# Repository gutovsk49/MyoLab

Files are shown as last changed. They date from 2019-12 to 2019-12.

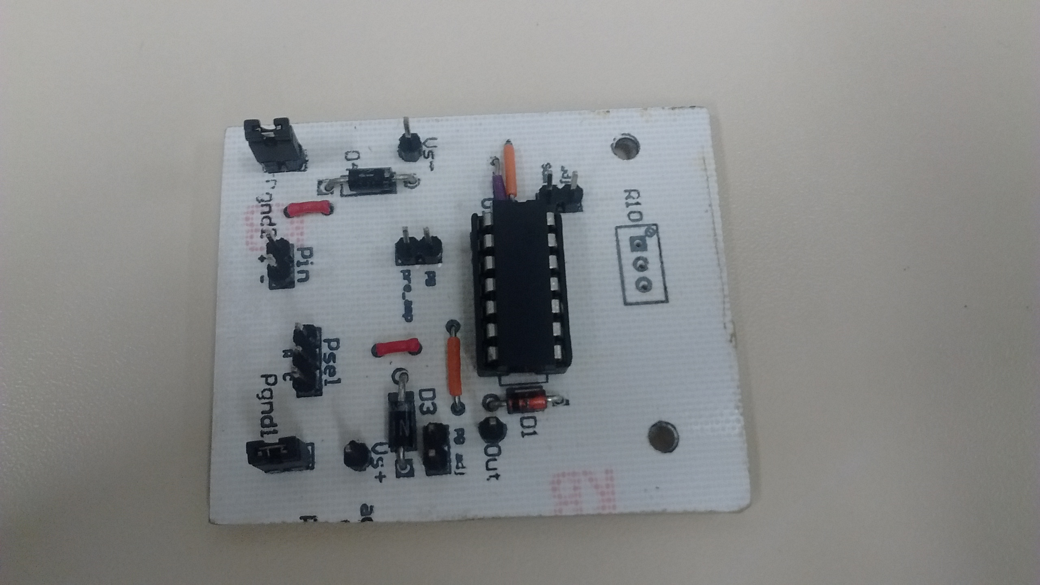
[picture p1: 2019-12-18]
prototipo_e_testes/IMG_20180618_203623081.jpg

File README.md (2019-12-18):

<h1> Sistema de aquisição de sinais elétricos musculares microcontrolado </h1>

<p>Repositorio criado para a disciplina de Projeto Integrador 3, do curso de engenharia eletrônica do IFSC - câmpus Florianópolis. <br/>
</p>

<h2> Revisão Bibliográfica </h2>

<p> A revisão bibliográfica pode ser acessada na wiki deste projeto.</p>
<p> A seguir, links de uma apresentação e um relatório técnico elaborados para outra disciplina, mas em cima do mesmo projeto, que podem ajudar na compreensão.<p>

[Apresentação - EMG](https://github.com/Everton-LF-Santos/Projeto-Integrador-3-2018-1/blob/Eletroneuromiografia-ENMG/prototipo_e_testes/Apresenta%C3%A7%C3%A3o%20PI3%20-%20COm.pdf)

[Relatório Técnico -EMG](https://docs.google.com/document/d/1B7dxLtk4YTgo0cG7-Vo4bE_Du3ThqNgDaQOGe45rIPg/edit)

<h2> Diagrama de blocos </h2>

Figura 1 - Diagrama de blocos do projeto Diagrama de Blocos

<h2> Pré-amplificador e filtro passa-alta </h2>
<p> Com a leitura das referências bilbiográficas da área feita e o diagrama de blocos definido, iniciou-se o desenvolvimento do projeto com o circuito de pré-amplificação. Foi encontrada no livro The Biomedical Engineering Book, uma topologia que junta o pré-amplificador e o filtro passa-alta no mesmo circuito. No exemplo da topologia, coincidentemente foi usado o INA118, mesmo amplificador de instrumentação disponível para o projeto. Na imagem a seguir, temos o esquemático simplificado e definição do ganho do componente.<p>
  
 Figura 2 - esquematico e ganho INA118 Esquemático simples e ganho INA118

<p>Foi arbitrado um ganho de 51 para a estrutura, por resultar em um valor de 1kohm para Rg, fácil de obter, e por ser um valor na faixa aceitável de ganho para esse tipo de estrutura neste tipo de aplicação, segundo a bibliografia estudada. A frequência de corte do passa-alta foi definida como 25 Hz, pois abaixo desse valor há ruídos de movimentação mecânica, e os diagramas de energia observados nas referências mostra a concentração de energia do sinal para a faixa acima deste valor.<p>
  
<p>Todas as considerações feitas, os cálculos e simulações pertinentes foram executados. Os arquivos de ambas etapas citadas estão disponível no link.<p>
  
Figura 3 - Circuito projetado Circuito projetado

[Calculos e Simulacoes - Pre_amp e PA](https://github.com/Everton-LF-Santos/Projeto-Integrador-3-2018-1/tree/Eletroneuromiografia-ENMG/pre_amp_e_passa_alta)

<h2> Filtro passa-baixa </h2>

<p>Com o primeiro bloco projetado, passou-se para o próximo bloco, o filtro passa-baixa. A topologia escolhida foi o filtro ativo Multiple Feedback com aproximação Butterworth. O ganho foi escolhido para 12,5 com o intuito de deixar o ganho em cascata da estrutura na casa das unidades de centenas. A frequência de corte de 250 Hz foi escolhida baseada no estudo dos diagramas de frequência do sinal  EMG. O ampop escolhido para implementar o circuito deste bloco foi o LM324, por atender as especificações de ganho e frequência e ser um componente de fácil obtenção e barato. Com os parâmetros do bloco definidos, passou-se então para os cálculos de componentes e simulações. Os arquivos pertinentes podem ser encontrados no link a seguir.<p>
  
Figura 4 - Circuito projetado Circuito projetado
  
[Calculos e Simulacoes - Filtro Passa-Baixa](https://github.com/Everton-LF-Santos/Projeto-Integrador-3-2018-1/tree/Eletroneuromiografia-ENMG/passa_baixa)

<h2> Somador DC </h2>

<p> A faixa de variação da amplitude do sinal elétrico muscular pode ser consideralmente ampla, devido fatores como tipo e qualidade dos eletrodos, grupo muscular em análise, capacidade e fisiologia do individuo em análise, entre outros. Levando isso em consideração, foi desenvolvido um bloco de ajuste de ganho, para que seja possível adequar o sinal adquirido da melhor forma possível.
<p>Porém, para fazer uma adequação correta, deve se conhecerou onde se está, e onde se quer chegar. O que temos são sinais da ordem de centenas de microvolts a unidades de milivolts. O que queremos é um sinal de saída analógico que pode ser convertido para informação digital, de preferência em um microncontrolador de baixo consumo. Estes geralmente trabalham com alimentação em 3.3 V. Logo, podemos definir que queremos um sinal de saída do módulo de aquisição que seja de 0 V a 3.3V, correspondente a sinais mioelétricos captados pelo eletrodo da ordem de 250uV até 5mV.
<p> Tendo o ponto de partida e de chegada, podemos focar esforços na construção do caminho. Para termos um sinal totalmente positivo na saída, é necessário que seja feito um offset DC no sinal. Para isso, foi escolhida a topologia de amplificador operacional na configuração não-inversora. Os valores de resistência do circuito foram arbitrados para não ter influencia no casamento de impedância dos blocos. A tensão de referência deste circuito (que deve ser metade da excursão do sinal de saída, logo, 3.3/2 = 1,65 V) será provida por um seguidor de tensão. Como o seguidor inverte a polaridade da tensão, o valor de -1,65V necessário é pego de um divisor resistivo entre o GND e o -5V da alimentação simétrica dos ampops.
<p> Tendo definido os parâmetros necessários, passaram-se para os demais cálculos e simulações do bloco de offset DC. Os arquivos relacionados a esta etapa podem ser encontrados no link.
  
Figura 5 - Circuito projetado Circuito projetado
  
[Calculos e Simulacoes - Somador DC](https://github.com/Everton-LF-Santos/Projeto-Integrador-3-2018-1/tree/Eletroneuromiografia-ENMG/somadorDC)

<h2> Ajuste de Ganho </h2>

<p> Devido a configuração e valores utilizados no bloco de offset DC, o sinal de entrada deste bloco deve variar de -0,815 V a +0,815 V para que haja 0 a 3.3V na saída. Com este faixa de amplitude necessária na entrada do bloco de offset, juntamente com a faixa de amplitude do sinal mioelétrico que deseja ser captada e conhecendo o ganho dos blocos anteriores, é possível finalmente projetar o bloco de ajuste de ganho. A topologia utilizada é simples, um amplificador operacional em configuração de ganho ajustável, com um trimpot conectado ao terminal inversor e na malha de realimentação e um diodo zener de 3.3V na saída para certificar que o valor máximo não seja ultrapassado. De acordo com os cálculos feitos, que podem ser observados nos arquivos desta etapa no link abaixo, o bloco de ajuste deve variar o ganho de aproximadamente 0,25 a 5. Conhecendo as impedâncias de entrada e saída dos blocos anteriores e posteriores, foram calculados os componentes necessários para que não houvesse influência na resposta em frequência do circuito. 
  
Figura 6 - Circuito projetado Circuito projetado
  
[Calculos e Simulacoes - Ajuste de ganho](https://github.com/Everton-LF-Santos/Projeto-Integrador-3-2018-1/tree/Eletroneuromiografia-ENMG/ajuste_ganho)
  
<h2> Prótotipo de aquisição e testes </h2>

<p> Com os quatro bloco de hardware de aquisição prontos, foi feito um protótipo para validar o funcionamento dos circuitos escolhidos. O esquemático e layout elaborados no software Altium Designer foram feitos em blocos, para garantir a validação individual de cada um, antes do teste coletivo. É possível acoplar os blocos por meio de jumpers. Após confeccionada a placa, foram feitos os testes pertinentes. Os resultados estão na apresentação de slides do link a seguir. Os outros arquivos relacionados à etapa de prototipagem e testes também podem ser encontrados no link.
  
Figura 7 - Blocos de hardware Blocos de hardware

Figura 8 - layout layout

Figura 9 - silk screen silk screen

Figura 10 - soldas SMD soldas SMD
  
[Protótipo  e teste do hardware de aquisição](https://github.com/Everton-LF-Santos/Projeto-Integrador-3-2018-1/tree/Eletroneuromiografia-ENMG/prototipo_e_testes)

<h2> Isolamento da rede e regulação de tensão </h2>

Com os resultados dos testes, foi concluído que os blocos do hardware de aquisição estavam de acordo com os requisitos necessários, porém para próxima etapa (teste IN VIVO), seria necessário que o circuito fosse alimentado de forma independente da rede elétrica. Assim, foi desenvolvida uma placa de regulação de tensão para alimentar o prototipo a partir de baterias 9 V. Os arquivos do projeto estão disponiveis no link a seguir.

[Placa de regulação de tensão](https://github.com/Everton-LF-Santos/Projeto-Integrador-3-2018-1/tree/Eletroneuromiografia-ENMG/reg_tensao)

<h2> Teste In Vivo </h2>

Com a alimentação regulada das baterias e sem interferência conduzida da rede elétrica, foi feito o teste In Vivo do hardware de aquisição. Usando eletrodos de Prata/Cloreto de Prata com gel condutor e cabos blindados, foi feita leitura do sinal da musculatura do antebraço esquerdo. O sinal foi observado por meio do osciloscópio portátil Rohde & Schwarz modelo RTH1004. Os arquivos relacionados a etapa de teste in vivo pode ser acessados pelo link a seguir.

[Teste In Vivo](https://github.com/Everton-LF-Santos/Projeto-Integrador-3-2018-1/tree/Eletroneuromiografia-ENMG/teste_vivo)

<h2> Teste In Vivo com transmissão dos dados </h2>

Por fim, foi iniciada a etapa de conversão analógica-digital transmissão dos dados, por meio do uso de um microcontrolador. Foi escolhido o chip ATMEGA328P pela experiência com desenvolvimentos anteriores. O código desenvolvido faz a conversão do sinal analógico em digital e envia o dado por meio do módulo Bluetooth HC-06. Para fins de facilitação de código, foi usada resolução de 8 bits na conversão A/D, com taxa de amostragem de 1 kHz. O uso de transmissão de dados sem fio é para garantir o isolamento galvânico do circuito de aquisição de qualquer outro equipamento eletrônico. Para visualização dos dados foi usado o software SerialPlot. Os arquivos relacionados a etapa de desenvolvimento do firmware, aquisição e visualização dos dados podem ser acessados no link a seguir.

[Teste In Vivo com aquisição de dados via Bluetooth](https://github.com/Everton-LF-Santos/Projeto-Integrador-3-2018-1/tree/Eletroneuromiografia-ENMG/firmware_bt)

<h2> Referências Bibliográficas </h2>

[link para arquivos das referências bibliográficas](https://drive.google.com/drive/u/1/folders/12AXk9AZwwBUo14S7_4OgoAu70kQn8SUb?ogsrc=32)

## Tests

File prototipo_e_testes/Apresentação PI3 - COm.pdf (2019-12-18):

# PROJETO INTEGRADOR III -MÓDULO DE AQUISIÇÃO DE SINAIS ELÉTRICOS MUSCULARES

Projeto IntegradorIII
Comunicação e Expressão
Augusto Daniel Rodrigues

## SUMÁRIO

- Sinais mioelétricos
- Condições de detecção de sinal
- Condicionamento de sinal
- Projeto dos blocos
- Esquemático, Layout e Hardware
- Testes dos blocos
- Referências

## SINAIS MIOELÉTRICOS

- Sinal sináptico -> axônio neuromotor -> potencial de ação;
- unidade motora;
- MUAP e MUAPT;
- Sinal EMG;

## SINAIS MIOELÉTRICOS

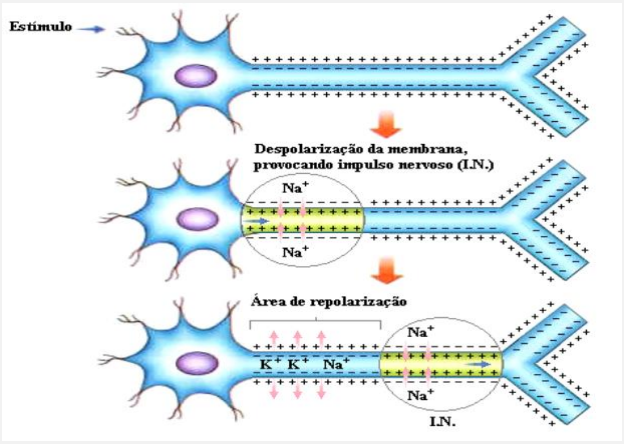
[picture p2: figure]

- Fonte:Vilela, 2004 apud Caparelli, 2007.

## SINAIS MIOELÉTRICOS

- Fonte:Vilela, 2004 apud Caparelli, 2007.

## SINAIS MIOELÉTRICOS

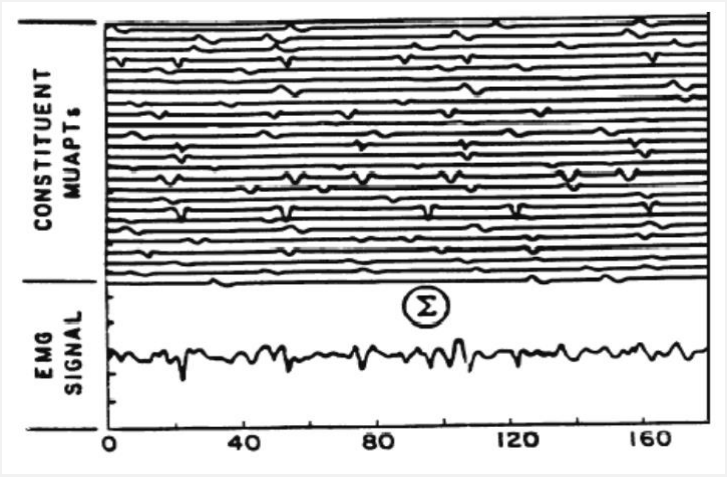
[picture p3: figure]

- Fonte: Basmajian; De Luca, 1985 apud Caparelli, 2007.

## CONDIÇÕES DE DETECÇÃO DO SINAL

- Eletrodos de agulha x eletrodos de superfície;
- Eletrodos passivos e ativos;
- 10mVpp e 10kHz x 5mVpp 250 Hz;
- Ruídos e interferências;
- Posicionamento dos eletrodos;
- Eletrodos de referência;
- Arranjos monopolar, bipolar, etc;

## CONDIÇÕES DE DETECÇÃO DO SINAL

- Ruídos e interferências;
- Cross Talk;
- Movimentos;
- EMI (rede elétrica);
- Componentes e técnicas de layout;

## SINAIS MIOELÉTRICOS

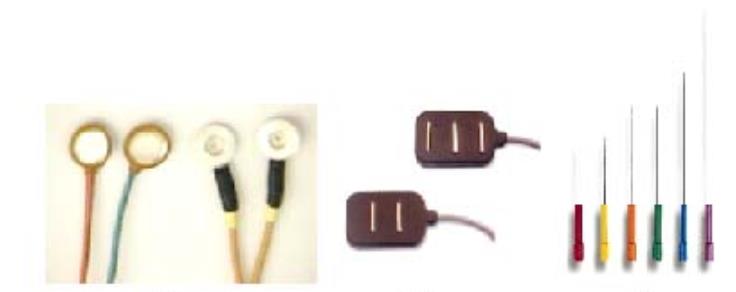
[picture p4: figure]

Fonte: Caparelli, 2007.

## SINAIS MIOELÉTRICOS

Fonte : https://www.primecirurgica.com.br/eletrodo-universal-red-dot-pct-c-50-unds-2570-3m-p760/

## SINAIS MIOELÉTRICOS

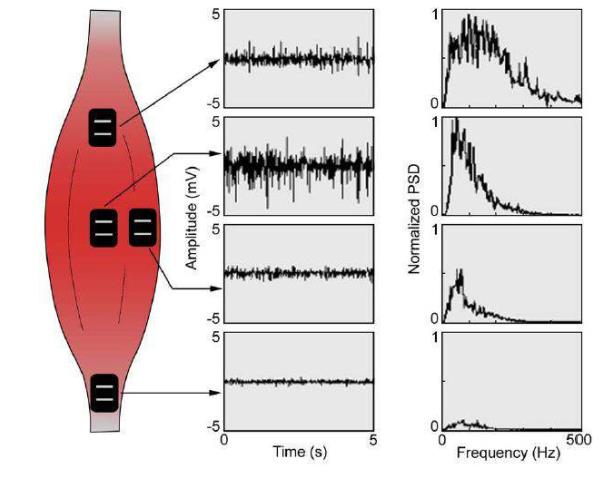
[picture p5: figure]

Fonte: Caparelli, 2007.

## CONDICIONAMENTO DO SINAL

- Amplificação do sinal;
- Filtragem em frequência;
- Offset DC;
- Conversão Analógica-Digital;
- Processamento;
- Visualização;

## CONDICIONAMENTO DO SINAL

- Amplificação do sinal;
- Amplificador de Instrumentação
- Amplificação diferencial;
- Alto CMRR;
- Ganho linear de até milhares de vezes;
- Alta impedância de entrada;

## CONDICIONAMENTO DO SINAL

Fonte: FRANCO, 1998 apud PEPINO, 2007.

## CONDICIONAMENTO DO SINAL

- Filtragem do sinal
- Anulação ou permissão do prosseguimento de um sinal em função de sua frequência;

## CONDICIONAMENTO DO SINAL

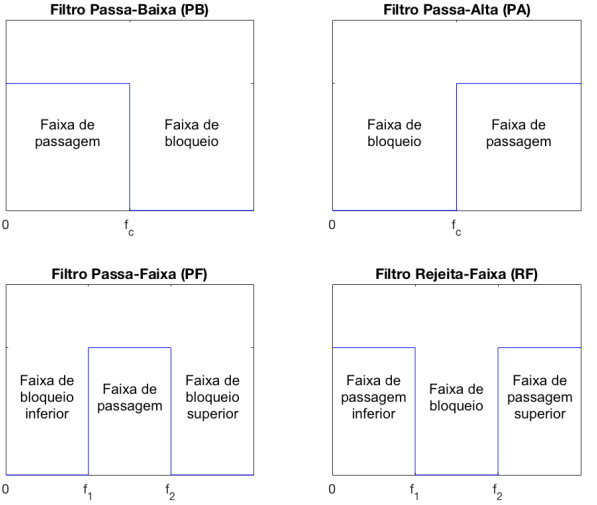
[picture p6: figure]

Fonte: LIMOLI (2017, p. 37).

## CONDICIONAMENTO DO SINAL

- Offset DC
- Elevação do nível de tensão do sinal;
- Sinal contínuo;
- Intervalo totalmente positivo (>=0);

## CONDICIONAMENTO DO SINAL

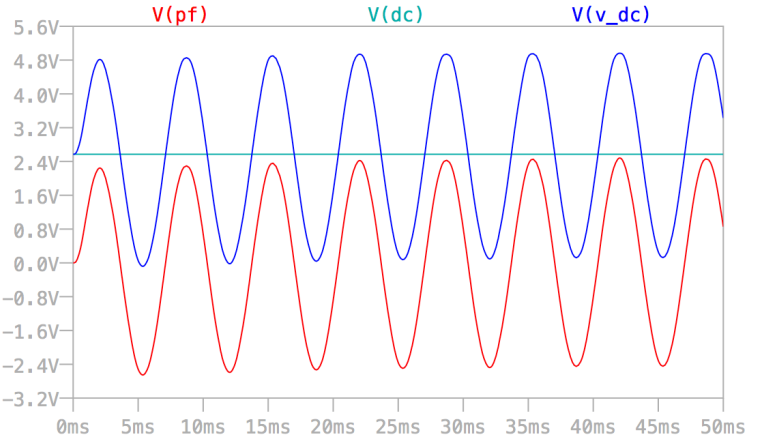
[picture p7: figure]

Fonte: LIMOLI (2017, p. 57).

## CONDICIONAMENTO DO SINAL

- Conversão Analógica-Digital
- Conversão de um nível de tensão para um conjunto de bits;
- Janela de conversão (1.1 V, 3.3 V, 5 V);
- Resolução da Conversão (nº de bits);
- Taxa de amostragem;

## CONDICIONAMENTO DO SINAL

Fonte: https://www.globalspec.com/learnmore/data_acquisition_signal_conditioning/signal_converting/analog_to_digital_converters

## PROJETO DOS BLOCOS

- Pré-requisitos / Parâmetros de projeto
- Conversão AD de 3.3 V 10 bits;
- Offset DC de 1,65 V;
- Janela de frequência de 25 Hz a 250 Hz;
- Considerar sinais da ordem de |250uV| à |5mV|;
- Ampop de instrumentação disponível = INA118;
- Ampop para demais circuitos = LM324N;
- Alimentação simétrica |5V| ( regulada de baterias de 9 V);

## PRÉ-AMPLIFICADOR + PASSA-ALTA

G = 51,
logo Rg = 1kΩ;

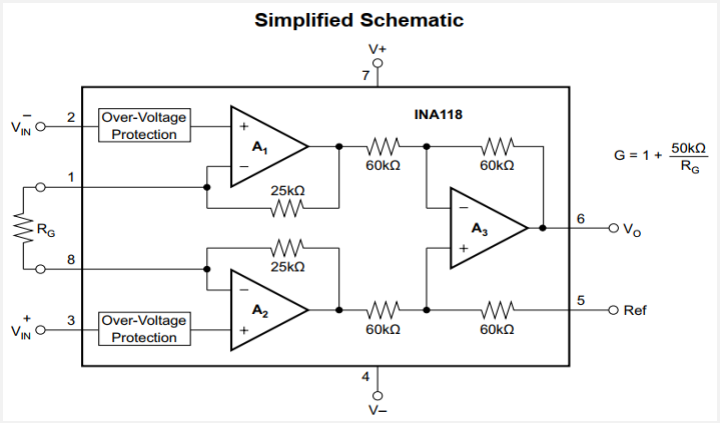
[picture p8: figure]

Fonte : Datasheet INA118. Disponível em : http://www.ti.com/lit/ds/symlink/ina118.pdf.

## PRÉ-AMPLIFICADOR + PASSA-ALTA

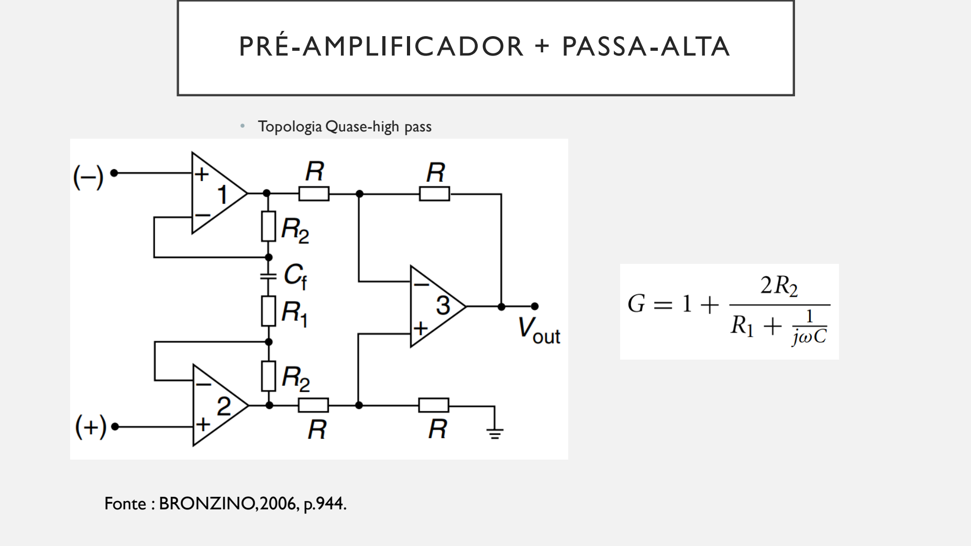
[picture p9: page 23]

- Topologia Quase-high pass

Fonte : BRONZINO, 2006, p.944.

## PRÉ-AMPLIFICADOR + PASSA-ALTA

Fonte: Do autor.

## PRÉ-AMPLIFICADOR + PASSA-ALTA

- Ganho = 51;
- Frequência de corte inferior = 25 Hz;
- C = 7 uF;

PRÉ -AMPLIFICADOR
+ PASSA-ALTA

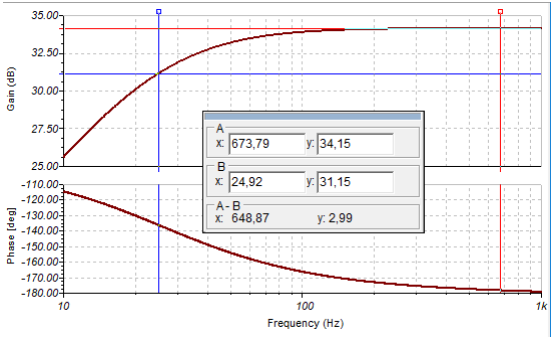
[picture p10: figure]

- Simulação
- 34,15 = 20*log(51)
- 31,15 = 20*log(51/√2)
- -3 dB;

Fonte: Do autor.

## PASSA-BAIXA

- Ganho = 12,5;
- Filtro ativo de 2ª ordem Multiple Feedback com aproximação Butterworth;
- Frequência de corte superior = 250 Hz;

## PASSA-BAIXA

Fonte: PERTENCE JR, Antônio (2003, p.184).

## PASSA-BAIXA

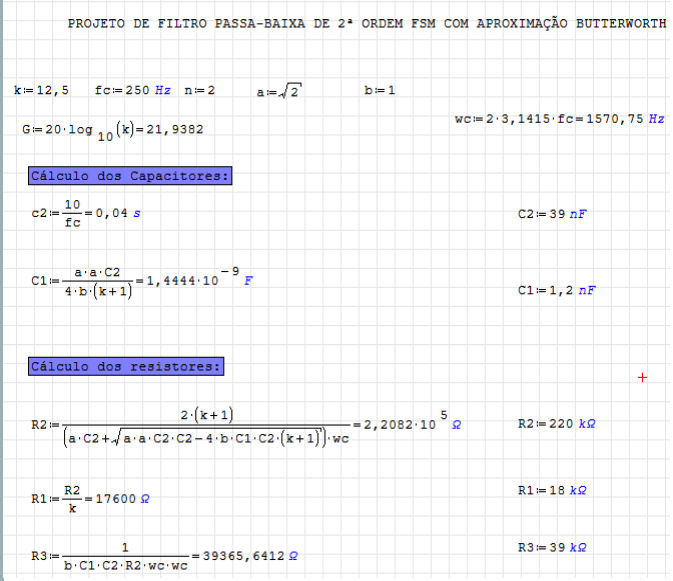
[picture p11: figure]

Fonte: Do autor.


## PASSA-BAIXA

- Simulação:
- Gs=10^(23,32/20) = 14,65
- Nova fc = 220 Hz (OK!)
- Ampop LM324N;

Fonte: Do autor.

## SOMADOR DC

- Saída de 0V a 3.3V;
- Buffer + somador não inversor;
- Capacitor de estabilização;
- Vref = 1,65V;
- Vout = 2*Vin +Vref, logo
- –0,815V <Vin < +0,815V
- Ampop LM324N;

Fonte: Do autor.

## SOMADOR DC

- Vref = -Vcc * R2 / (R1 + R2);
- R1 = 2,03*R2;
- R1 = 680k e R2 = 330k, Vref = 1,63 V;


Fonte: Do autor.

## AJUSTE DE GANHO

- Ganho do primeiro bloco = 51;
- Ganho do primeiro bloco = 12,5;
- Ganho em cascata = 637,5;
- Ganho máximo:
- |250uV| * 637,5 = 0,159375;
- 0,815 / 0,159375 = 5,11;
- Ganho mínimo:
- |5mV| * 637,5 = 3,1875;
- 0,815 / 3,1875 = 0,256;

## AJUSTE DE GANHO


- Capacitor de acoplamento AC;
- Situação 1:
- 56k/220k = 0,254;
- Situação 2:
- 1056k/220k = 4,8;

Fonte: Do autor.

## ESQUEMÁTICO, LAYOUT E HARDWARE

Fonte: Do autor.

## ESQUEMÁTICO, LAYOUT E HARDWARE


Fonte: Do autor.

## ESQUEMÁTICO, LAYOUT E HARDWARE


## ESQUEMÁTICO, LAYOUT E HARDWARE

Fonte: Do autor.

## ESQUEMÁTICO, LAYOUT E HARDWARE


Fonte: Do autor.

## ESQUEMÁTICO, LAYOUT E HARDWARE

Fonte: Do autor. | Fonte: Do autor. | Fonte: Do autor.

## ESQUEMÁTICO, LAYOUT E HARDWARE


Fonte: Do autor. | Fonte: Do autor.

## TESTES DOS BLOCOS


- Pré-amplificador + passa-alta:
- 3,68 / 77,6e-3 = 47,42;
- 500 Hz;
Fonte: Do autor. | Fonte: Do autor.

## TESTES DOS BLOCOS


- Pré-amplificador + passa-alta:
- 2,48 / 77,6e-3 = 31,96 ~= 47,42*0,707;
- ~27 Hz;
Fonte: Do autor. | Fonte: Do autor.

## TESTES DOS BLOCOS


- Passa-Baixa:
- 3,56/ 0,320 = 11,125;
- ~100 Hz;
Fonte: Do autor. | Fonte: Do autor.

## TESTES DOS BLOCOS

- Passa-Baixa:
- 3,72/ 0,316 = 11,77;
- ~27 Hz;


Fonte: Do autor.

## TESTES DOS BLOCOS

- Passa-Baixa:
- 2,60/ 0,318 = 8,17 ~= 11,77*0,707;
- ~250 Hz;

Fonte: Do autor.

## TESTES DOS BLOCOS

- Ajuste de Ganho:
- 2,90/ 0,624 = 4,64;


- ~150 Hz; | Fonte: Do autor.

## TESTES DOS BLOCOS

- Ajuste de Ganho:
- 0,556 / 2,06 = 0,269;


- ~150 Hz; | Fonte: Do autor.

## TESTES DOS BLOCOS


- Somador DC:
Fonte: Do autor. | Fonte: Do autor.

## OBRIGADO!

Augusto Daniel Rodrigues

augusto.dr@aluno.ifsc.edu.br

## REFERÊNCIAS

BRONZINO, Joseph D. The Biomedical Engineering Handbook: Medical Devices and Systems. 3th ed. Hartford. Taylor and Francis, 2006.
Disponível em:https://brainmaster.com/software/pubs/brain/The_Biomedical_Engineering_Handbook_.pdf

CAPARELLI, Thiago B. Projeto e desenvolvimento de um sistema multicanal de biotelemetria para detecção de sinais ECG, EEG e EMG. 2007. 109 p. Dissertação (Pós-graduação em Engenharia Elétrica) - Faculdade de Engenharia Elétrica, Universidade Federal de Uberlândia, Uberlândia.
Disponível em:https://repositorio.ufu.br/handle/123456789/14636

DE LUCA, Carlo J; BASMAJIAN, John V. Muscles Alive: Their functions revealed by eletromyography. 5th ed. Baltimore: Willians andWilkins, 1985.

LIMOLI, Camila S. Protótipo de um eletromiógrafo sem fio de baixo custo. 2017. 75 p. Trabalho de Conclusão de Curso (Graduação no Curso de Engenharia Elétrica com Ênfase em Eletrônica) - Escola de Engenharia de São Carlos, Universidade de São Paulo. - São Carlos.
Disponível em : http://www.tcc.sc.usp.br/tce/disponiveis/18/180450/tce-29052017-162649/?&lang=br

## REFERÊNCIAS

PEPINO, André L.G. Sistema de controle de Dispositivos Através de EMG(Eletromiografia). 2007. 90p. Monografia de Conclusão de Curso (Graduação em Engenharia da Computação) - Núcleo de Ciências Exatas e Tecnológicas, Centro Universitário Positivo. Curitiba.
Disponível em:https://www.up.edu.br/blogs/engenharia-da-computacao/wp-content/.../2007.1.pdf

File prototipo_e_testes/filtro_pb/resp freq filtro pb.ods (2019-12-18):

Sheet: teste 1 - filtro pb
f | Vin | Vout | G
1.000000 | 0,152 | 0,58 | 3,82
1.300000 | 0,152 | 0,62 | 4,08
1.690000 | 0,148 | 0,68 | 4,59
2.197000 | 0,148 | 0,66 | 4,46
2.856100 | 0,154 | 0,68 | 4,42
3.712930 | 0,152 | 0,7 | 4,61
4.826809 | 0,158 | 0,72 | 4,56
6.274852 | 0,156 | 0,68 | 4,36
8.157308 | 0,154 | 0,68 | 4,42
10.604500 | 0,166 | 0,68 | 4,10
13.785850 | 0,168 | 0,7 | 4,17
17.921604 | 0,168 | 0,68 | 4,05
23.298086 | 0,148 | 0,7 | 4,73
30.287512 | 0,148 | 0,7 | 4,73
39.373764 | 0,15 | 0,68 | 4,53
51.185894 | 0,16 | 0,7 | 4,38
66.541664 | 0,17 | 0,7 | 4,12
86.504166 | 0,156 | 0,68 | 4,36
112.455414 | 0,15 | 0,66 | 4,40
146.192032 | 0,168 | 0,64 | 3,81
190.049637 | 0,164 | 0,6 | 3,66
247.064529 | 0,158 | 0,5 | 3,16
321.183899 | 0,158 | 0,44 | 2,78
417.539063 | 0,158 | 0,3 | 1,90
542.800781 | 0,182 | 0,24 | 1,32
705.640991 | 0,16 | 0,16 | 1,00
917.333313 | 0,172 | 0,14 | 0,81
1192.533325 | 0,16 | 0,1 | 0,63
1550.293335 | 0,154 | 0,1 | 0,65
2015.381348 | 0,168 | 0,1 | 0,60
2619.995850 | 0,148 | 0,1 | 0,68
3405.994629 | 0,16 | 0,1 | 0,63
4427.792969 | 0,168 | 0,07 | 0,42
5756.130859 | 0,156 | 0,1 | 0,64
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

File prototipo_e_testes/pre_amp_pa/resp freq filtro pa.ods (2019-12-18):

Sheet: teste 1 - filtro pa + preamp
f | Vin | Vout | G
1.000000 | 0,202 | 0,32 | 1,58415841584158
1.300000 | 0,198 | 0,32 | 1,61616161616162
1.690000 | 0,19 | 0,48 | 2,52631578947368
2.197000 | 0,22 | 0,48 | 2,18181818181818
2.856100 | 0,182 | 0,48 | 2,63736263736264
3.712930 | 0,178 | 0,72 | 4,04494382022472
4.826809 | 0,184 | 0,64 | 3,47826086956522
6.274852 | 0,186 | 0,8 | 4,30107526881721
8.157308 | 0,202 | 0,96 | 4,75247524752475
10.604500 | 0,206 | 1,12 | 5,4368932038835
13.785850 | 0,228 | 1,44 | 6,31578947368421
17.921604 | 0,22 | 1,6 | 7,27272727272727
23.298086 | 0,204 | 1,92 | 9,41176470588235
30.287512 | 0,216 | 2,08 | 9,62962962962963
39.373764 | 0,204 | 2,24 | 10,9803921568627
51.185894 | 0,214 | 2,48 | 11,588785046729
66.541664 | 0,212 | 2,56 | 12,0754716981132
86.504166 | 0,202 | 2,72 | 13,4653465346535
112.455414 | 0,224 | 2,78 | 12,4107142857143
146.192032 | 0,212 | 2,7 | 12,7358490566038
190.049637 | 0,198 | 2,8 | 14,1414141414141
247.064529 | 0,202 | 2,8 | 13,8613861386139
321.183899 | 0,204 | 2,88 | 14,1176470588235
417.539063 | 0,21 | 2,88 | 13,7142857142857
542.800781 | 0,194 | 2,88 | 14,8453608247423
705.640991 | 0,23 | 2,88 | 12,5217391304348
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

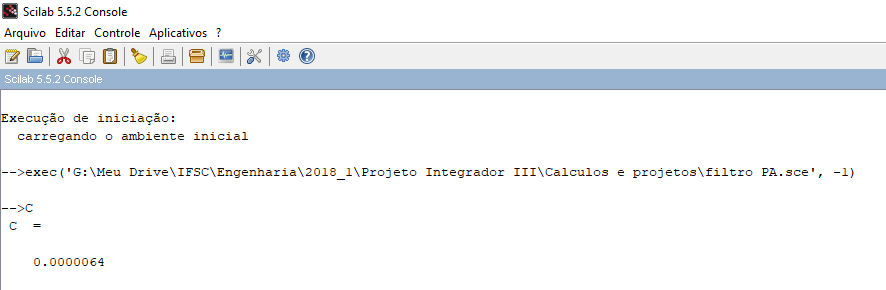
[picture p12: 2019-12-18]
images/result_scilab_pa.png

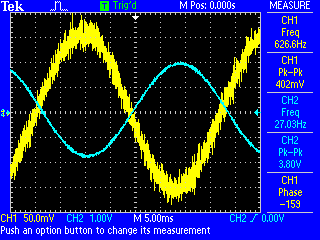
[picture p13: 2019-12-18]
prototipo_e_testes/filtro_pb/TEK0004.BMP

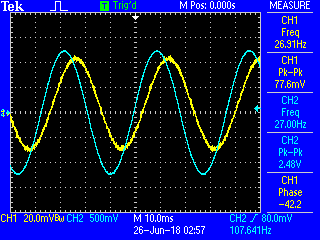
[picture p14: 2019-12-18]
prototipo_e_testes/pre_amp_pa/TEK0005.BMP

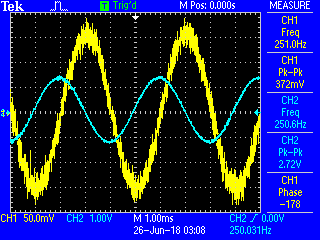
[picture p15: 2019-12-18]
prototipo_e_testes/filtro_pb/TEK0007.BMP

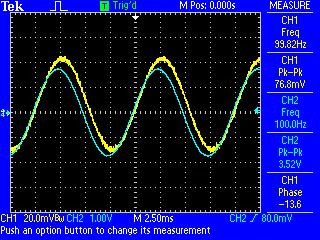
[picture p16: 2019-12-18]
prototipo_e_testes/pre_amp_pa/TEK0003.BMP

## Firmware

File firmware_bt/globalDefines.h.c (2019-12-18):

/* -----------------------------------------------------------------------------
 * Project:			GPDSE AVR8 Integrated Library
 * File:			globalDefines.h
 * Module:			Global definitions file for the GAIL Project
 * Author:			Leandro Schwarz
 * Version:			12.3
 * Last edition:	2016-01-15
 * ---------------------------------------------------------------------------*/

#ifndef __GLOBALDEFINES_H
#define __GLOBALDEFINES_H 123

// -----------------------------------------------------------------------------
// Basic definitions -----------------------------------------------------------

#ifndef F_CPU
	#define F_CPU 16000000UL
#endif

// -----------------------------------------------------------------------------
// Header files ----------------------------------------------------------------

#include <avr/io.h>
#include <avr/interrupt.h>
#include <util/delay.h>
#include <stdio.h>

// -----------------------------------------------------------------------------
// Constant definitions --------------------------------------------------------

// -----------------------------------------------------------------------------
// Bit handling macro functions ------------------------------------------------

#ifndef setBit
	#define setBit(reg, bit)					((reg) |= (1 << (bit)))
#endif
#ifndef clrBit
	#define clrBit(reg, bit)					((reg) &= ~(1 << (bit)))
#endif
#ifndef cplBit
	#define cplBit(reg, bit)					((reg) ^= (1 << (bit)))
#endif
#ifndef isBitSet
	#define isBitSet(reg, bit)					(((reg) >> (bit)) & 1)
#endif
#ifndef isBitClr
	#define isBitClr(reg, bit)					(!(((reg) >> (bit)) & 1))
#endif
#ifndef waitUntilBitIsSet
	#define waitUntilBitIsSet(reg, bit)			do{}while(isBitClr((reg), (bit)))
#endif
#ifndef waitUntilBitIsClear
	#define waitUntilBitIsClear(reg, bit)		do{}while(isBitSet((reg), (bit)))
#endif
#ifndef noOperation
	#define noOperation(cycles)					__builtin_avr_delay_cycles(cycles)
#endif
#ifndef setMask
	#define setMask(reg, mask, offset)			((reg) |= ((mask) << (offset)))
#endif
#ifndef clrMask
	#define clrMask(reg, mask, offset)			((reg) &= ~((mask) << (offset)))
#endif
#ifndef cplMask
	#define cplMask(reg, mask, offset)			((reg) ^= ((mask) << (offset)))
#endif

// -----------------------------------------------------------------------------
// New data types --------------------------------------------------------------

typedef char				int8;
typedef int					int16;
typedef long int			int32;
typedef long long			int64;
typedef unsigned char		uint8;
typedef unsigned int		uint16;
typedef unsigned long int	uint32;
typedef unsigned long long	uint64;

typedef enum bool_t{
	FALSE = 0,
	TRUE = 1
} bool_t;

typedef enum logic_t{
	LOW = 0,
	HIGH = 1,
	OFF = 0,
	ON = 1
} logic_t;

typedef enum direction_t{
	LEFT = 0,
	RIGHT = 1,
	UP = 0,
	DOWN = 1,
	CLOCKWISE = 0,
	COUNTERCLOCKWISE = 1
} direction_t;

typedef enum resultValue_t{
	RESULT_OK = 0,
	RESULT_PORT_VALUE_UNSUPPORTED,
	RESULT_INT_SENSE_VALUE_UNSUPPORTED,
	RESULT_TIMER_PRESCALER_VALUE_UNSUPPORTED,
	RESULT_TIMER_MODE_VALUE_UNSUPPORTED,

	RESULT_USART_PARITY_UNSUPORTED,
	RESULT_USART_BAUD_RATE_UNSUPORTED,
	RESULT_UNSUPPORTED_VALUE
} resultValue_t;

typedef enum usartError_t{
	USART_OK = 1,
	USART_FRAME_ERROR = 2,
	USART_PARITY_ERROR  = 4,
	USART_BUFFER_OVERFLOW_ERROR = 8
} usartError_t;

typedef enum systemPrescalerValue_t{
	SYSTEM_PRESCALER_OFF = 0,
	SYSTEM_PRESCALER_2 = 1,
	SYSTEM_PRESCALER_4 = 2,
	SYSTEM_PRESCALER_8 = 3,
	SYSTEM_PRESCALER_16 = 4,
	SYSTEM_PRESCALER_32 = 5,
	SYSTEM_PRESCALER_64 = 6,
	SYSTEM_PRESCALER_128 = 7,
	SYSTEM_PRESCALER_256 = 8
} systemPrescalerValue_t;

typedef enum eepromMode_t{
	EEPROM_ERASE_WRITE = 0,
	EEPROM_ERASE_ONLY,
	EEPROM_WITE_ONLY
} eepromMode_t;

typedef enum portMode_t{
	PORT_OUTPUT_LOW = 0,
	PORT_OUTPUT_HIGH,
	PORT_INPUT_TRISTATE,
	PORT_INPUT_PULL_UP,
	PORT_NO_CHANGE = 255
} portMode_t;

typedef enum senseMode_t{
	SENSE_LOW_LEVEL = 0,
	SENSE_ANY_EDGE,
	SENSE_FALLING_EDGE,
	SENSE_RISING_EDGE,
	SENSE_NO_CHANGE = 255
} senseMode_t;

typedef enum timerModeA_t{
	TIMER_A_MODE_NORMAL= 0,
	TIMER_A_MODE_PWM_PHASE_CORRECTED_MAX = 1,
	TIMER_A_MODE_CTC = 2,
	TIMER_A_MODE_FAST_PWM_MAX = 3,
	TIMER_A_MODE_PWM_PHASE_CORRECTED_OCRA = 5,
	TIMER_A_MODE_FAST_PWM_OCRA = 7,
	TIMER_A_MODE_NO_CHANGE = 255
} timerModeA_t;

typedef enum timerModeB_t{
	TIMER_B_MODE_NORMAL = 0,
	TIMER_B_MODE_PWM_PHASE_CORRECTED_8_BITS = 1,
	TIMER_B_MODE_PWM_PHASE_CORRECTED_9_BITS = 2,
	TIMER_B_MODE_PWM_PHASE_CORRECTED_10_BITS = 3,
	TIMER_B_MODE_CTC = 4,
	TIMER_B_MODE_FAST_PWM_8_BITS = 5,
	TIMER_B_MODE_FAST_PWM_9_BITS = 6,
	TIMER_B_MODE_FAST_PWM_10_BITS = 7,
	TIMER_B_MODE_PWM_PHASE_FREQUENCY_CORRECTED_ICR = 8,
	TIMER_B_MODE_PWM_PHASE_FREQUENCY_CORRECTED_OCRA = 9,
	TIMER_B_MODE_PWM_PHASE_CORRECTED_ICR = 10,
	TIMER_B_MODE_PWM_PHASE_CORRECTED_OCRA = 11,
	TIMER_B_MODE_CTC_ICR = 12,
	TIMER_B_MODE_FAST_PWM_ICR = 14,
	TIMER_B_MODE_FAST_PWM_OCRA = 15,
	TIMER_B_MODE_NO_CHANGE = 255
} timerModeB_t;

typedef enum timerPrescalerValueA_t{
	TIMER_A_CLOCK_DISABLE = 0,
	TIMER_A_PRESCALER_OFF = 1,
	TIMER_A_PRESCALER_8 = 2,
	TIMER_A_PRESCALER_64 = 3,
	TIMER_A_PRESCALER_256 = 4,
	TIMER_A_PRESCALER_1024 = 5,
	TIMER_A_PRESCALER_T0_FALLING_EDGE = 6,
	TIMER_A_PRESCALER_T0_RISING_EDGE = 7,
	TIMER_A_PRESCALER_NO_CHANGE = 255
} timerPrescalerValueA_t;

typedef enum timerPrescalerValueB_t{
	TIMER_B_CLOCK_DISABLE = 0,
	TIMER_B_PRESCALER_OFF = 1,
	TIMER_B_PRESCALER_8 = 2,
	TIMER_B_PRESCALER_32 = 3,
	TIMER_B_PRESCALER_64 = 4,
	TIMER_B_PRESCALER_128 = 5,
	TIMER_B_PRESCALER_256 = 6,
	TIMER_B_PRESCALER_1024 = 7,
	TIMER_B_PRESCALER_NO_CHANGE = 255
} timerPrescalerValueB_t;

typedef enum timerOutput_t{
	TIMER_PORT_NORMAL = 0,
	TIMER_PORT_TOGGLE_ON_COMPARE = 1,
	TIMER_PORT_CLEAR_ON_COMPARE = 2,
	TIMER_PORT_SET_ON_COMPARE = 3,
	TIMER_PORT_NON_INVERTING_MODE = 2,
	TIMER_PORT_INVERTING_MODE = 3,
	TIMER_PORT_NO_CHANGE = 255
} timerOutput_t;

typedef enum timerInputCaptureNoiseCanceler_t{
	TIMER_NOISE_CANCELER_OFF = 0,
	TIMER_NOISE_CANCELER_FALLING_EDGE = 1,
	TIMER_NOISE_CANCELER_RISING_EDGE = 3
} timerInputCaptureNoiseCanceler_t;

typedef enum adcPrescaler_t{
	ADC_PRESCALER_OFF = 0,
	ADC_PRESCALER_2 = 1,
	ADC_PRESCALER_4 = 2,
	ADC_PRESCALER_8 = 3,
	ADC_PRESCALER_16 = 4,
	ADC_PRESCALER_32 = 5,
	ADC_PRESCALER_64 = 6,
	ADC_PRESCALER_128 = 7,
	ADC_PRESCALER_NO_CHANGE = 255
} adcPrescaler_t;

typedef enum adcReference_t{
	ADC_REFERENCE_EXTERNAL = 0,
	ADC_REFERENCE_POWER_SUPPLY = 1,
	ADC_REFERENCE_INTERNAL = 3,
	ADC_REFERENCE_NO_CHANGE = 255
} adcReference_t;

typedef enum adcChannel_t{
	ADC_CHANNEL_0 = 0,
	ADC_CHANNEL_1 = 1,
	ADC_CHANNEL_2 = 2,
	ADC_CHANNEL_3 = 3,
	ADC_CHANNEL_4 = 4,
	ADC_CHANNEL_5 = 5,
	ADC_CHANNEL_6 = 6,
	ADC_CHANNEL_7 = 7,
	ADC_CHANNEL_TEMPERATURE = 8,
	ADC_CHANNEL_BAND_GAP = 14,
	ADC_CHANNEL_GND = 15,
	ADC_CHANNEL_NO_CHANGE = 255
} adcChannel_t;

typedef enum adcMode_t{
	ADC_MODE_SINGLE_CONVERSION = 0,
	ADC_MODE_AUTO_CONTINUOUS,
	ADC_MODE_AUTO_ANALOG_COMP,
	ADC_MODE_AUTO_INT0,
	ADC_MODE_AUTO_TIMER0_COMPA,
	ADC_MODE_AUTO_TIMER0_OVERFLOW,
	ADC_MODE_AUTO_TIMER1_COMPB,
	ADC_MODE_AUTO_TIMER1_OVERFLOW,
	ADC_MODE_AUTO_TIMER1_CAPTURE,
	ADC_MODE_NO_CHANGE = 255
} adcMode_t;

typedef enum adcDataPresentation_t{
	ADC_LEFT_ADJUSTED = 0,
	ADC_RIGHT_ADJUSTED
} adcDataPresentation_t;

typedef enum usartDataBits_t{
	USART_DATA_BITS_5 = 0,
	USART_DATA_BITS_6,
	USART_DATA_BITS_7,
	USART_DATA_BITS_8,
	USART_DATA_BITS_9,
	USART_DATA_BITS_NO_CHANGE = 255
} usartDataBits_t;

typedef enum usartStopBits_t{
	USART_STOP_BIT_SINGLE = 0,
	USART_STOP_BIT_DOUBLE,
	USART_STOP_BIT_NO_CHANGE = 255
} usartStopBits_t;

typedef enum usartParity_t{
	USART_PARITY_NONE = 0,
	USART_PARITY_ODD,
	USART_PARITY_EVEN,
	USART_PARITY_MARK,
	USART_PARITY_SPACE,
	USART_PARITY_NO_CHANGE = 255
} usartParity_t;

typedef enum usartMode_t{
	USART_MODE_ASYNCHRONOUS = 0,
	USART_MODE_ASYNCHRONOUS_DOUBLE_SPEED,
	USART_MODE_SYNCHRONOUS_XCK_FALLING,
	USART_MODE_SYNCHRONOUS_XCK_RISING,
	USART_MODE_SYNCHRONOUS_SPI,
	USART_MODE_NO_CHANGE = 255
} usartMode_t;

typedef enum usartBaudRate_t{
	USART_BAUD_600 = 600UL,
	USART_BAUD_1200 = 1200UL,
	USART_BAUD_2400 = 2400UL,
	USART_BAUD_4800 = 4800UL,
	USART_BAUD_9600 = 9600UL,
	USART_BAUD_14400 = 14400UL,
	USART_BAUD_19200 = 19200UL,
	USART_BAUD_28800 = 28800UL,
	USART_BAUD_38400 = 38400UL,
	USART_BAUD_56000 = 56000UL,
	USART_BAUD_57600 = 57600UL,
	USART_BAUD_115200 = 115200UL,
	USART_BAUD_128000 = 128000UL,
	USART_BAUD_256000 = 256000UL,
	USART_BAUD_NO_CHANGE = 0xFFFFFFFFUL
} usartBaudRate_t;

#endif

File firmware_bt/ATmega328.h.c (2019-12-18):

/* -----------------------------------------------------------------------------
 * Project:			GPDSE AVR8 Library
 * File:			ATmega328.h
 * Module:			ATmega328 basic interface
 * Author:			Leandro Schwarz
 * Version:			12.2
 * Last edition:	2016-01-15
 * -------------------------------------------------------------------------- */

#ifndef __ATMEGA328_H
#define __ATMEGA328_H 122

// -----------------------------------------------------------------------------
// Microcontroller constant identifier -----------------------------------------

#define MCU	_ATMEGA328_

// -----------------------------------------------------------------------------
// Header files ----------------------------------------------------------------

#include "globalDefines.h"
#if __GLOBALDEFINES_H < 123
	#error Error 100 - The defintion file is outdated (globalDefines must be version 12.3 or greater).
#endif
#include <avr/io.h>
#include <util/atomic.h>
#include <stdio.h>

// -----------------------------------------------------------------------------
// Some definitions that seemed to be forgotten in avr/io.h ---------------------

#ifndef SPMEN
	#define SPMEN	0
#endif

// -----------------------------------------------------------------------------
// New data types --------------------------------------------------------------

#define USART_RECEIVER_BUFFER_SIZE 50UL
extern FILE usartStream;
extern uint8 usartReceiverBuffer[USART_RECEIVER_BUFFER_SIZE];
extern uint8 usartReceiverBufferNextRead;
extern uint8 usartReceiverBufferNextWrite;
extern uint8 usartReceiverBufferLength;

// -----------------------------------------------------------------------------
// Status register -------------------------------------------------------------

void	globalInterruptEnable(void);
void	globalInterruptDisable(void);

// -----------------------------------------------------------------------------
// System clock prescaler ------------------------------------------------------

resultValue_t	systemClockSetPrescaler(systemPrescalerValue_t prescaler);

// -----------------------------------------------------------------------------
// EEPROM memory ---------------------------------------------------------------

#define EEPROM_ADDRESS_MASK	0x03FF

void	eepromSetOperationMode(eepromMode_t mode);
void	eepromReadyActivateInterrupt(void);
void	eepromReadyDeactivateInterrupt(void);
uint8	eepromRead(uint16 address);
void	eepromWrite(uint16 address, uint8 data);

// -----------------------------------------------------------------------------
// Pull-Up ---------------------------------------------------------------------

void	globalPullUpDisable(void);
void	globalPullUpEnable(void);

// -----------------------------------------------------------------------------
// External interrupts ---------------------------------------------------------

// INT0
resultValue_t	int0Config(portMode_t port, senseMode_t sense);
void			int0ActivateInterrupt(void);
void			int0DeactivateInterrupt(void);
void			int0ClearInterruptRequest(void);

// INT1
resultValue_t	int1Config(portMode_t port, senseMode_t sense);
void			int1ActivateInterrupt(void);
void			int1DeactivateInterrupt(void);
void			int1ClearInterruptRequest(void);

// PCINT7-0
void			pcint7_0Enable(void);
void			pcint7_0Disable(void);
void			pcint7_0ClearInterruptRequest(void);
resultValue_t	pcint0ActivateInterrupt(portMode_t port);
void			pcint0DeactivateInterrupt(void);
resultValue_t	pcint1ActivateInterrupt(portMode_t port);
void			pcint1DeactivateInterrupt(void);
resultValue_t	pcint2ActivateInterrupt(portMode_t port);
void			pcint2DeactivateInterrupt(void);
resultValue_t	pcint3ActivateInterrupt(portMode_t port);
void			pcint3DeactivateInterrupt(void);
resultValue_t	pcint4ActivateInterrupt(portMode_t port);
void			pcint4DeactivateInterrupt(void);
resultValue_t	pcint5ActivateInterrupt(portMode_t port);
void			pcint5DeactivateInterrupt(void);
resultValue_t	pcint6ActivateInterrupt(portMode_t port);
void			pcint6DeactivateInterrupt(void);
resultValue_t	pcint7ActivateInterrupt(portMode_t port);
void			pcint7DeactivateInterrupt(void);

// PCINT14-8
void			pcint14_8Enable(void);
void			pcint14_8Disable(void);
void			pcint14_8ClearInterruptRequest(void);
resultValue_t	pcint8ActivateInterrupt(portMode_t port);
void			pcint8DeactivateInterrupt(void);
resultValue_t	pcint9ActivateInterrupt(portMode_t port);
void			pcint9DeactivateInterrupt(void);
resultValue_t	pcint10ActivateInterrupt(portMode_t port);
void			pcint10DeactivateInterrupt(void);
resultValue_t	pcint11ActivateInterrupt(portMode_t port);
void			pcint11DeactivateInterrupt(void);
resultValue_t	pcint12ActivateInterrupt(portMode_t port);
void			pcint12DeactivateInterrupt(void);
resultValue_t	pcint13ActivateInterrupt(portMode_t port);
void			pcint13DeactivateInterrupt(void);
resultValue_t	pcint14ActivateInterrupt(portMode_t port);
void			pcint14DeactivateInterrupt(void);

// PCINT23-16
void			pcint23_16Enable(void);
void			pcint23_16Disable(void);
void			pcint23_16ClearInterruptRequest(void);
resultValue_t	pcint16ActivateInterrupt(portMode_t port);
void			pcint16DeactivateInterrupt(void);
resultValue_t	pcint17ActivateInterrupt(portMode_t port);
void			pcint17DeactivateInterrupt(void);
resultValue_t	pcint18ActivateInterrupt(portMode_t port);
void			pcint18DeactivateInterrupt(void);
resultValue_t	pcint19ActivateInterrupt(portMode_t port);
void			pcint19DeactivateInterrupt(void);
resultValue_t	pcint20ActivateInterrupt(portMode_t port);
void			pcint20DeactivateInterrupt(void);
resultValue_t	pcint21ActivateInterrupt(portMode_t port);
void			pcint21DeactivateInterrupt(void);
resultValue_t	pcint22ActivateInterrupt(portMode_t port);
void			pcint22DeactivateInterrupt(void);
resultValue_t	pcint23ActivateInterrupt(portMode_t port);
void			pcint23DeactivateInterrupt(void);


// -----------------------------------------------------------------------------
// Timer/counter 0 -------------------------------------------------------------
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
